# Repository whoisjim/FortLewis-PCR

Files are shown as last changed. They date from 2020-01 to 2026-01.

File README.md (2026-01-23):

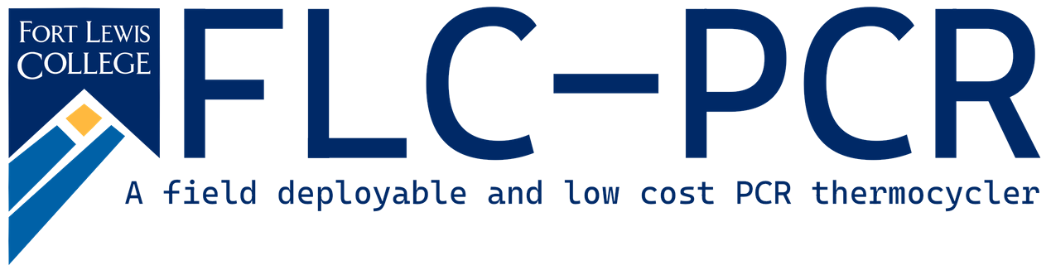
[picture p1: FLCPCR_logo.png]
FLCPCR logo


FLC-PCR is a field deployable and low cost PCR thermocycler developed by students at Fort Lewis College. Polymerase chain reaction (PCR) is the process of duplicating a strand of DNA millions of times. After the DNA has been amplified analysis can be performed to detect pathogens and other DNA related characteristics. Performing PCR on a strand of DNA involves placing the sample in a chemical solution. Then repeating the raising and lowering the temperature duplicates the DNA. Raising the temperature splits the strands and lowering the temperature allows the chemicals to reform the other half of each DNA strand.

## Student Members

- James Ferguson
- Jesse Duran
- Wesley Killinen
- Gavin Wakefield
- Farjana Showme

## Faculty Advisors

- Jason Wagner
- Caroline Kulesza
- Christie Chatterley
- Yiyan Li

## Folder Descriptions

- **CAD:** SOLIDWORKS design files for the the lid and heating block.
- **Circuts:** EAGLE PCB design files for the  PCB microcontroller.
- **DataRecordingAndGraphing:** Recorded data and python scripts for graphing and analysis.
- **Papers:** Project documentation that was presented at weekly meetings or conferences etc.
- **Parts:** Datasheets for components.
- **Software:** The programs that run on the FLC-PCR system.

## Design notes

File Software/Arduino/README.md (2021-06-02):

# Arduino software

The three ATmega328p scripts are as follows.

- PCRControl

  Manages the moment to moment temperature. Control of the system is performed through serial UART communication.

- Serial Commands

  - `whoami\n` prints an identification string.
  - `d\n` request a data point form the system of the format `[Block Temperature] [PWM] [Lid Temperature]\n`.
  - `verbose\n` toggles sending a data point of every tic of the format `[Block Temperature] [PWM] [Lid Temperature]\n`.
  - `pid\n` toggles sending a data point of every tic of the format `[Target Temperature] [Block Temperature] [PWM]\n`.
  - `state\n` sends `0\n` of peltier off, `1\n` for peltier on.
  - `offl\n` Turns the lid off.
  - `offp\n` Turns the peltier off.
  - `off\n` Turns the peltier and lid off.
  - `onl\n` Turns the lid on.
  - `onp\n` Turns the peltier on.
  - `on\n` Turns the peltier and lid on.
  - `pt[value]\n` Sets the target block temperature
  - `pia[value]\n` Sets the weighting for the Block Temperature moving average. 1 is minimum.
  - `poa[value]\n` Sets the weighting for the PWM moving average. 1 is the minimum.
  - `plc[value]\n` Sets the low bound for PWM. -255 is the minimum.
  - `plh[value]\n` Sets the high bound for PWM. 255 is the maximum.

- PCRDummy

  Fakes PCRControl missing some commands. Out of data

- EfficiencyTest

  For measuring System power consumption and thermal output. Does not work with FLC-PCR PCB rev1.

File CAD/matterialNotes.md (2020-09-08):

# materials
[link wiki](https://en.wikipedia.org/wiki/List_of_thermal_conductivities)
[link toolbox](https://www.engineeringtoolbox.com/insulation-temperatures-d_922.html)
## Polyurethane foam 
too low maximum temperature
## Silica aerogel
too hard to make, too expensive, too fragile

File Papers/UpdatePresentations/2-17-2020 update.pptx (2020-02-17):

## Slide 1

Old Block

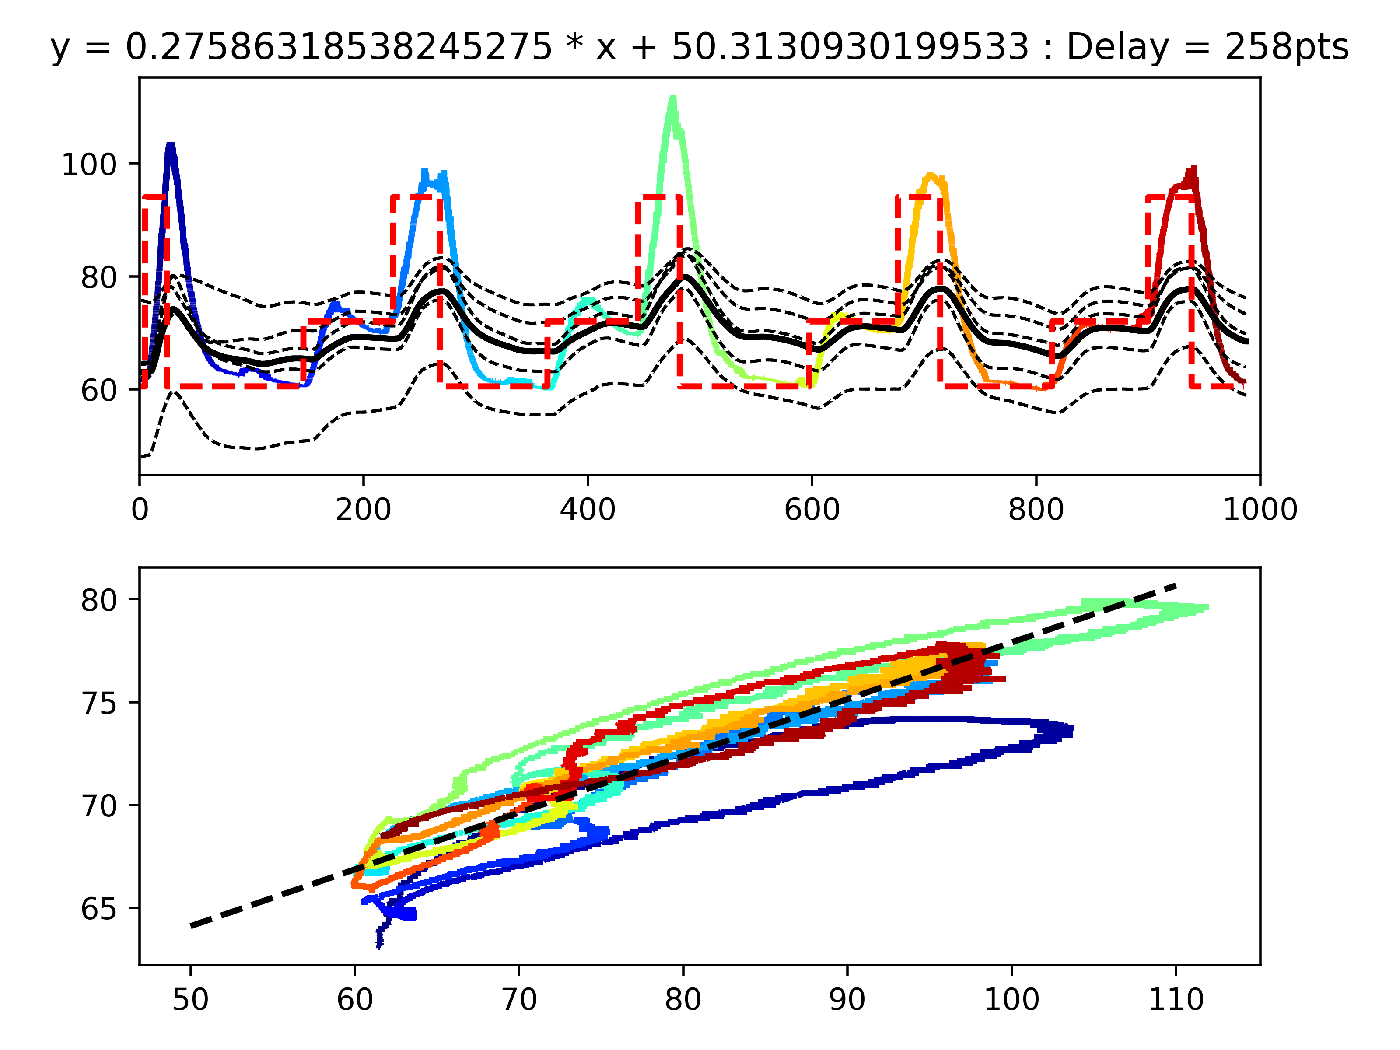
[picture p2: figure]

Bio Rad Block

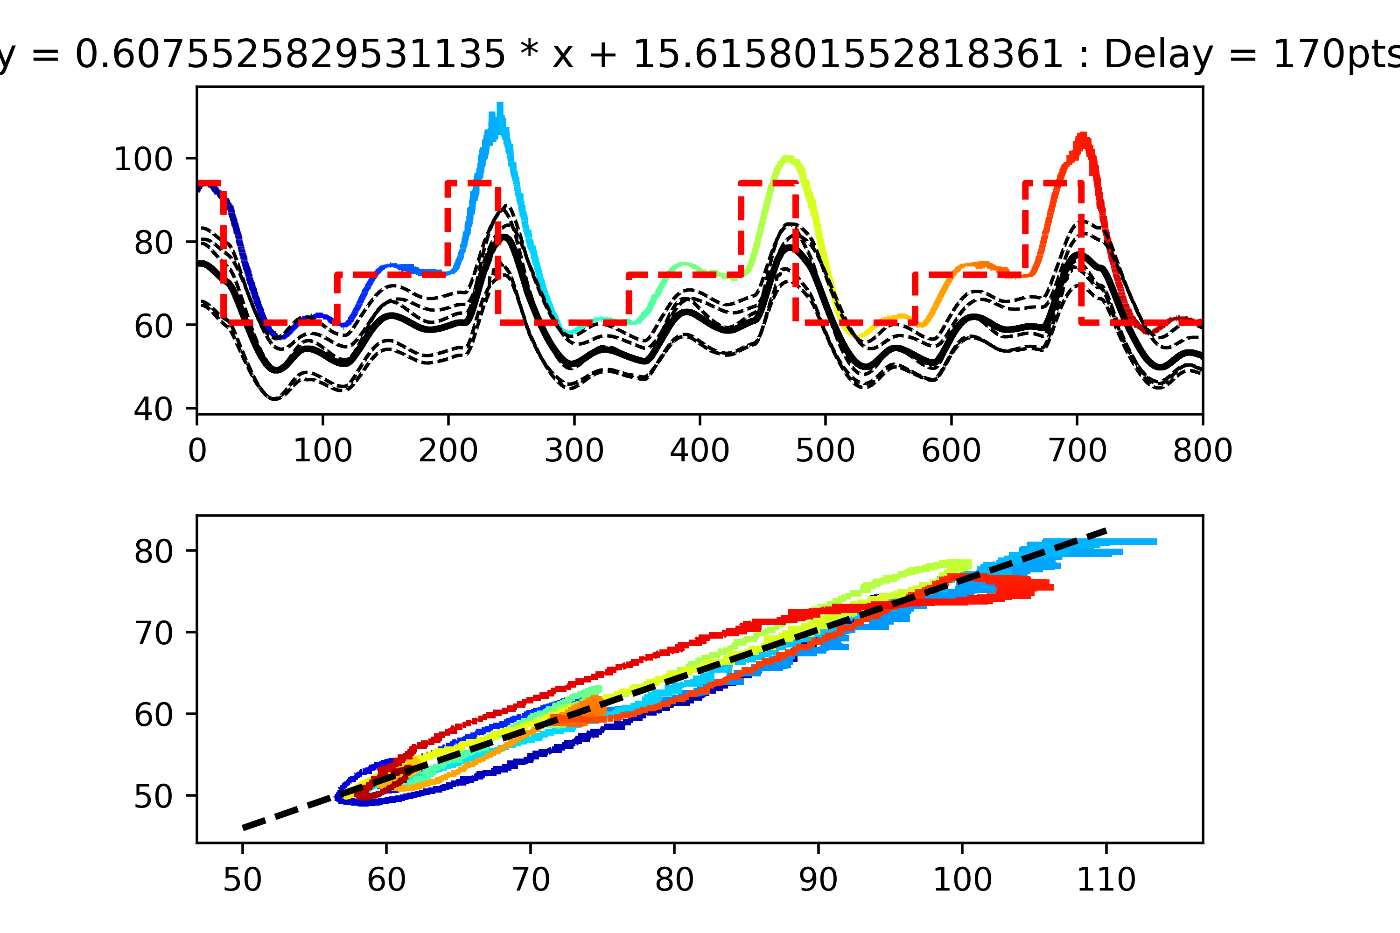
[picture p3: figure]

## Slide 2

After Calibration

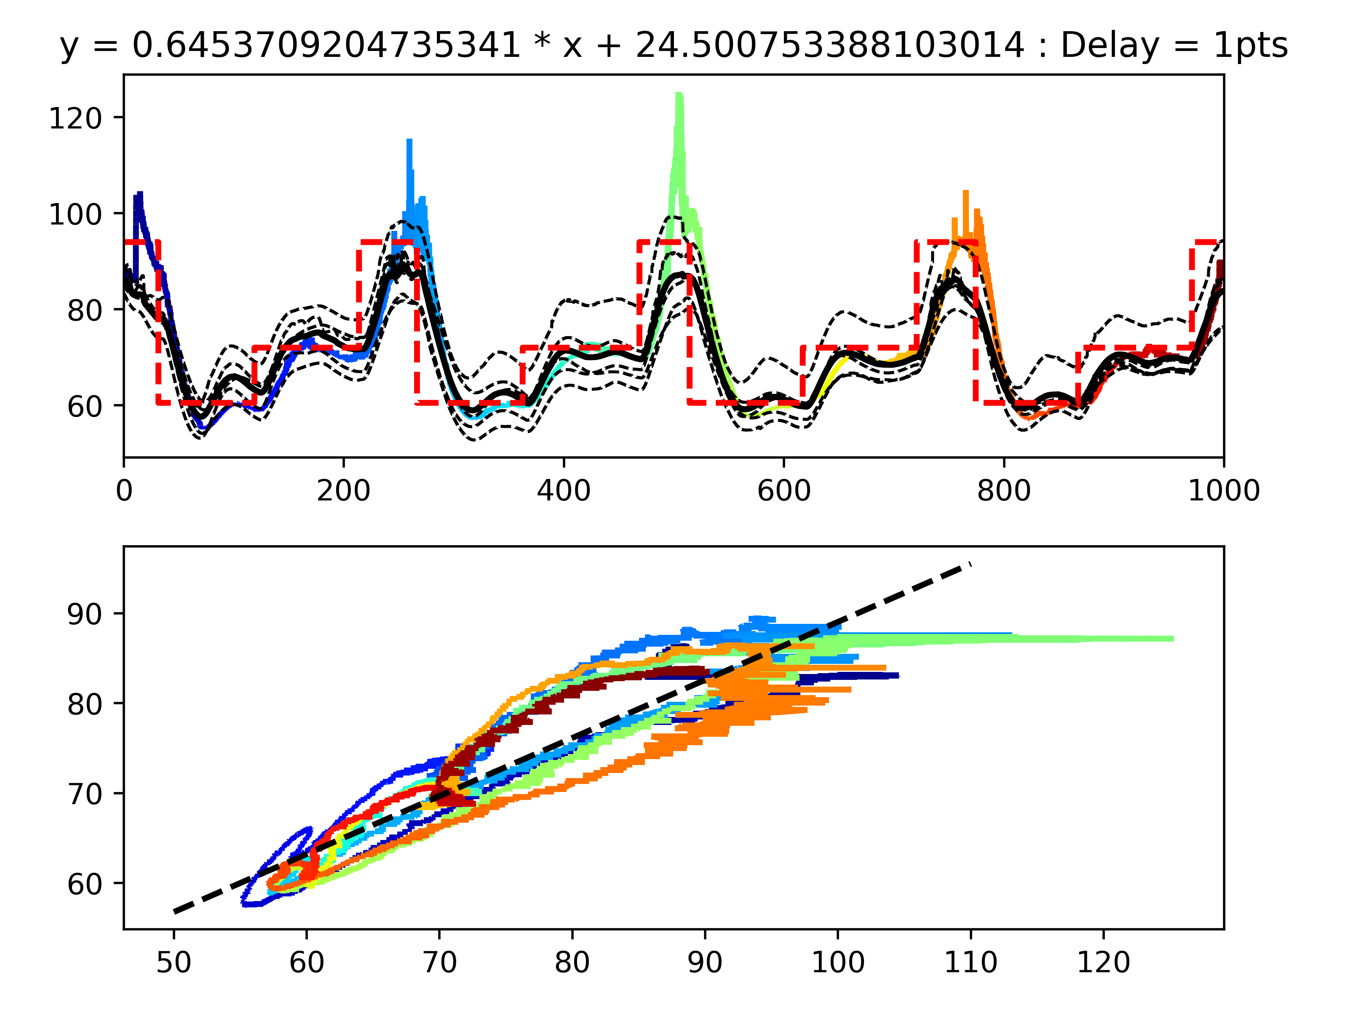
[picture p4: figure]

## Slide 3

Touch Screen Concept

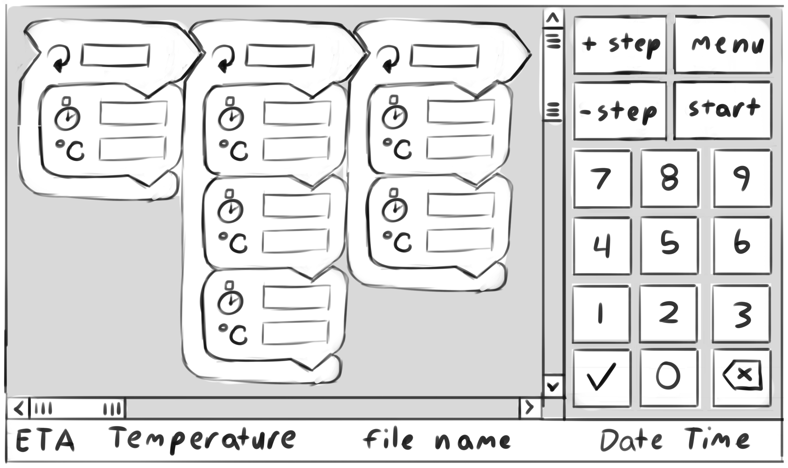
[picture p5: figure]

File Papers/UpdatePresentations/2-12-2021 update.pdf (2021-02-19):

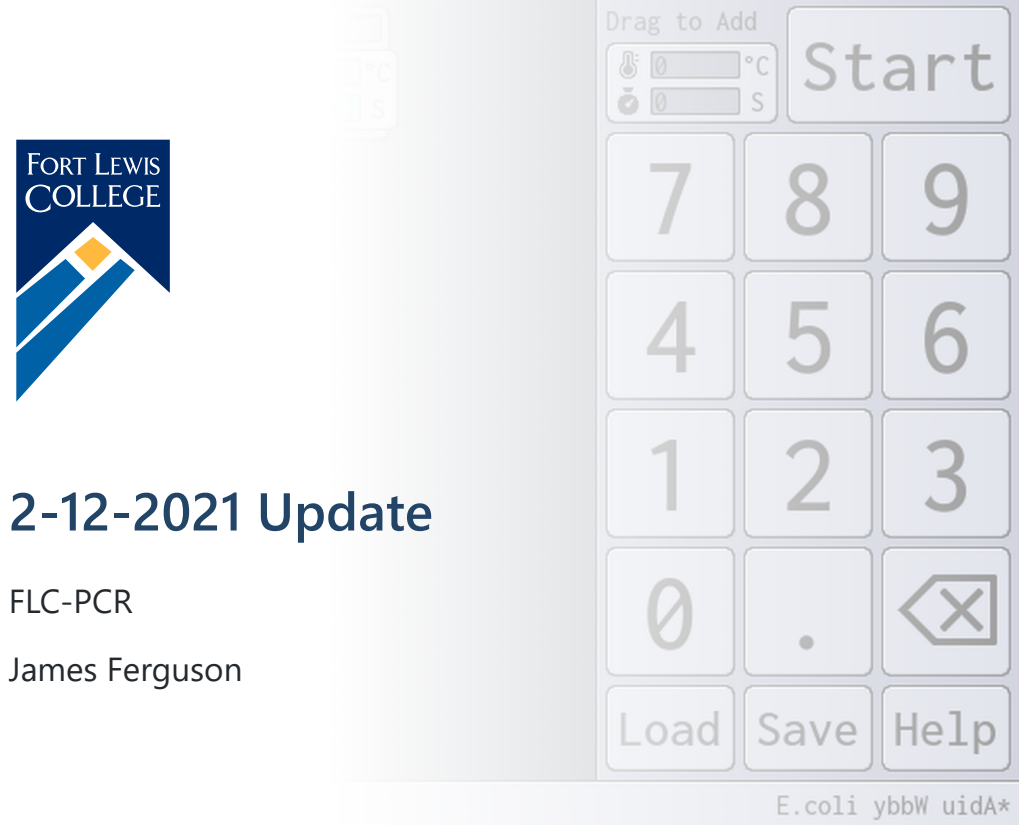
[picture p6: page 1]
2-12-2021 Update; FLC-PCR; James Ferguson

## Last Week

Cleaned lab
Wired thermistors and SSR

## Todo

Finish wiring
Mount Pi and display
Cut holes for vents, switch and power Re-run temperature calibration
Run PCR experiment
Finish fixing UI blocking bug

## End

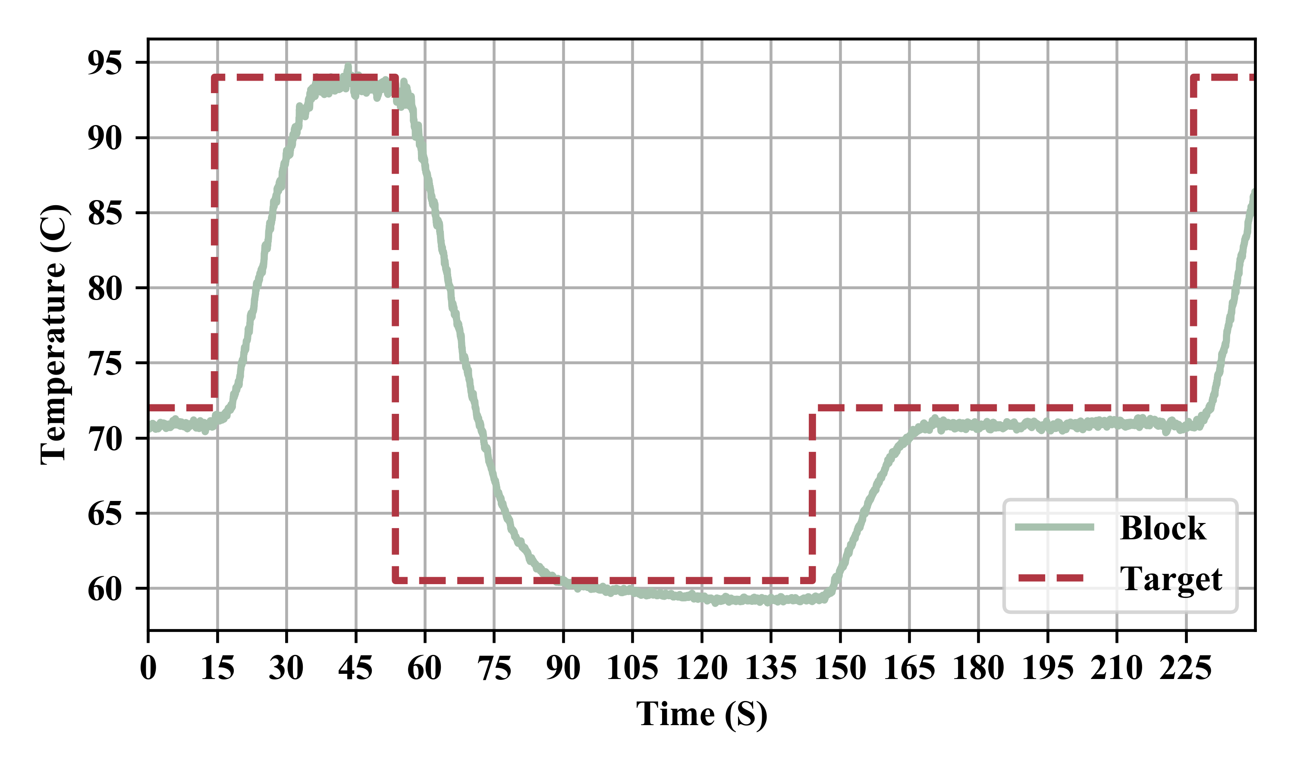
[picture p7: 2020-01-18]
Papers/IEEE_EMBC_2020/CycleTemp.png

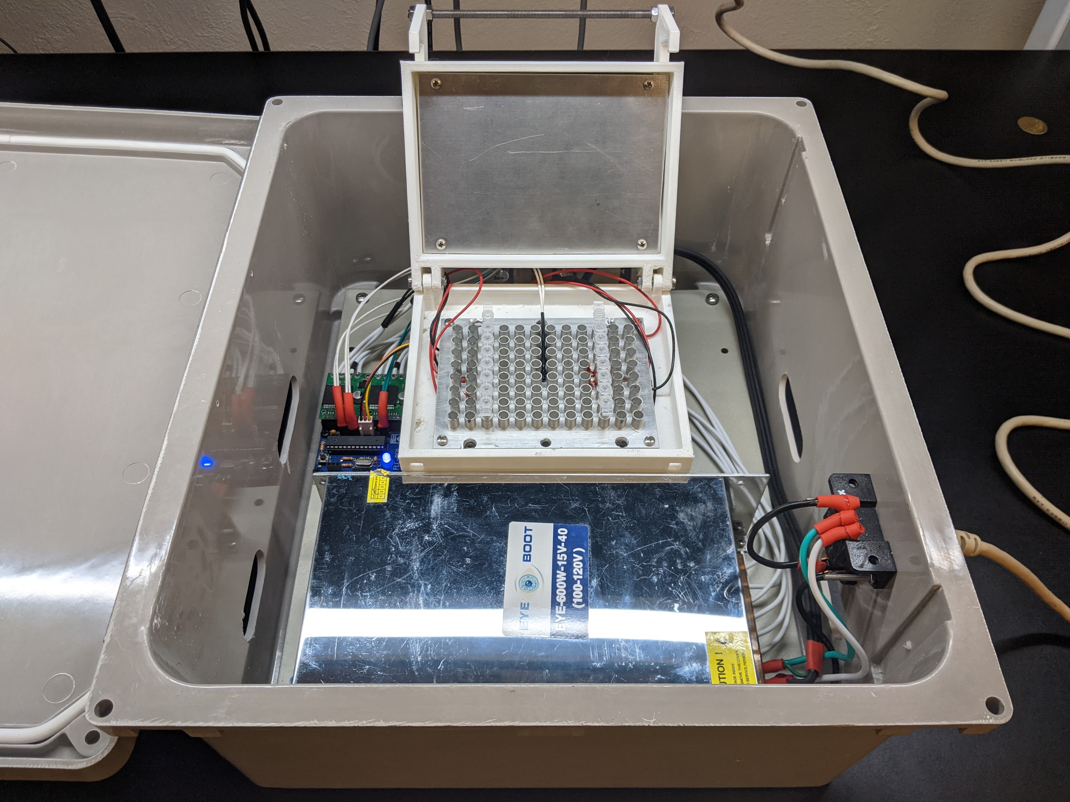
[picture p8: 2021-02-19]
Papers/MiscFigures/OpenLid.jpg

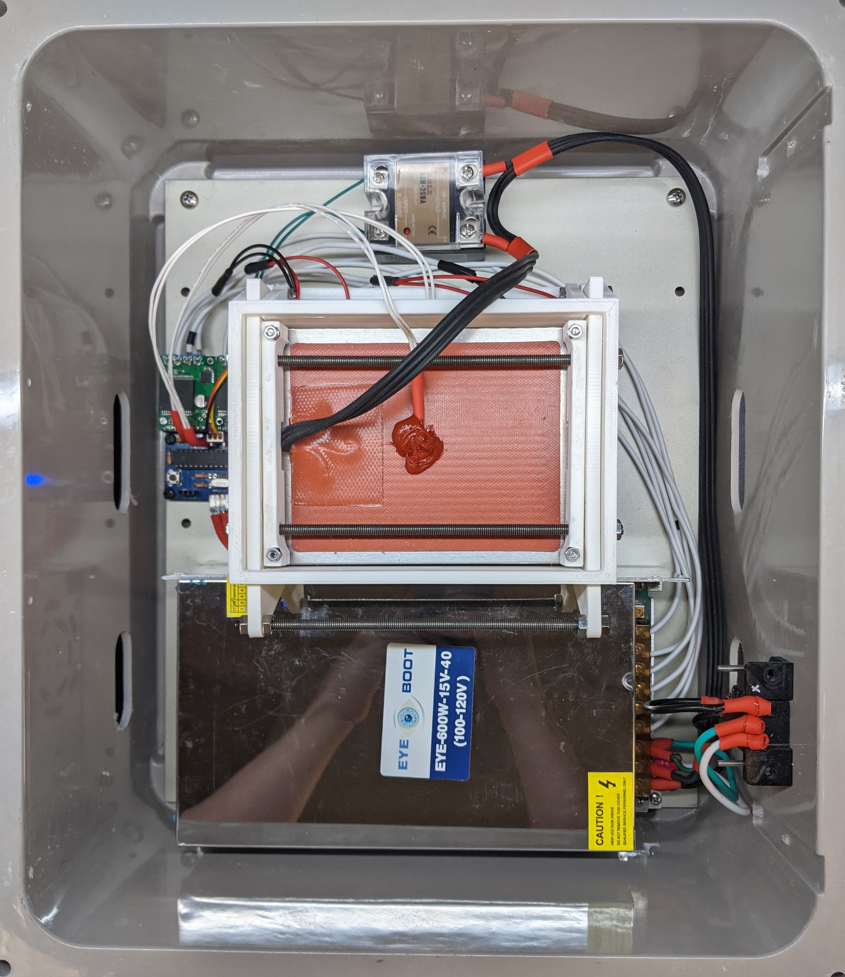
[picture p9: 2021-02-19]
Papers/MiscFigures/TopDonw.jpg

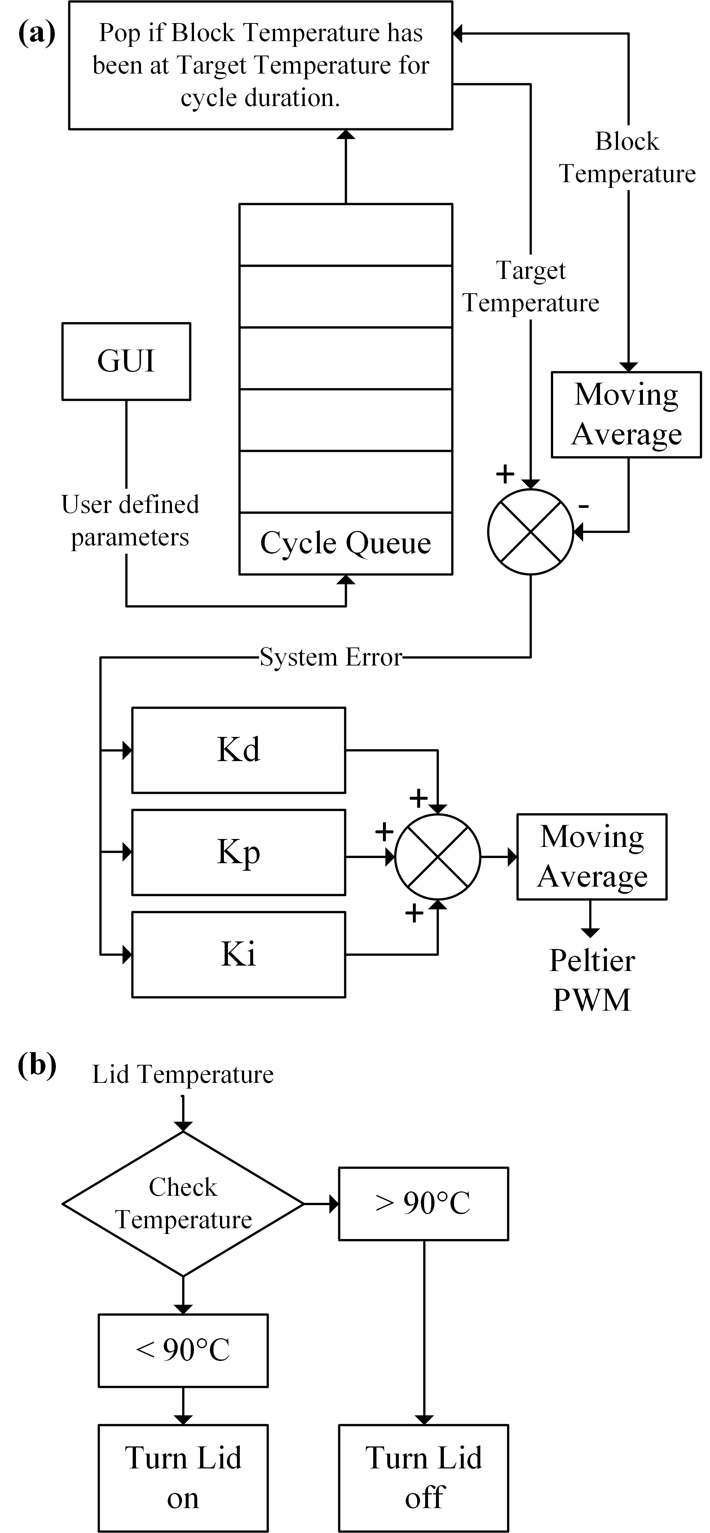
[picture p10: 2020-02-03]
Papers/IEEE_EMBC_2020/SoftwareFigure.png

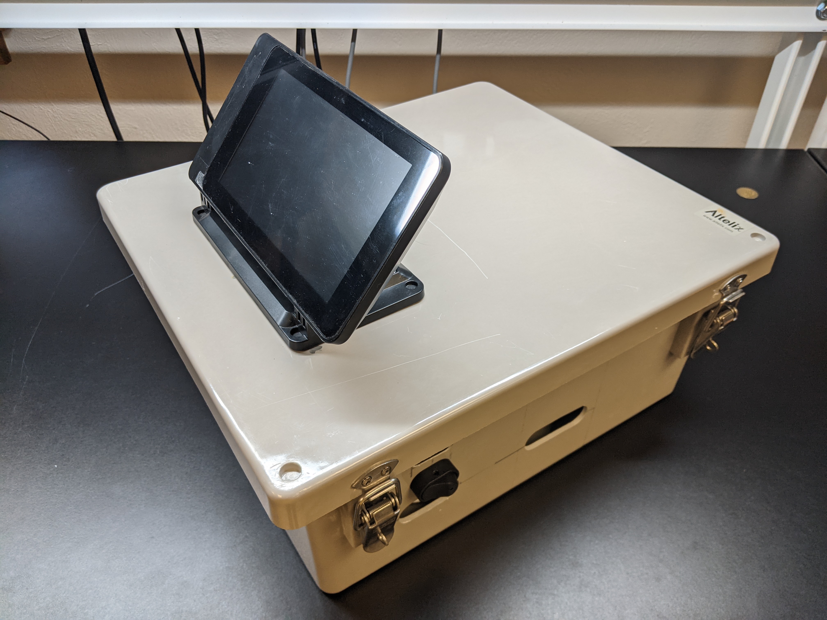
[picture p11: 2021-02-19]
Papers/MiscFigures/ClosedBox.jpg

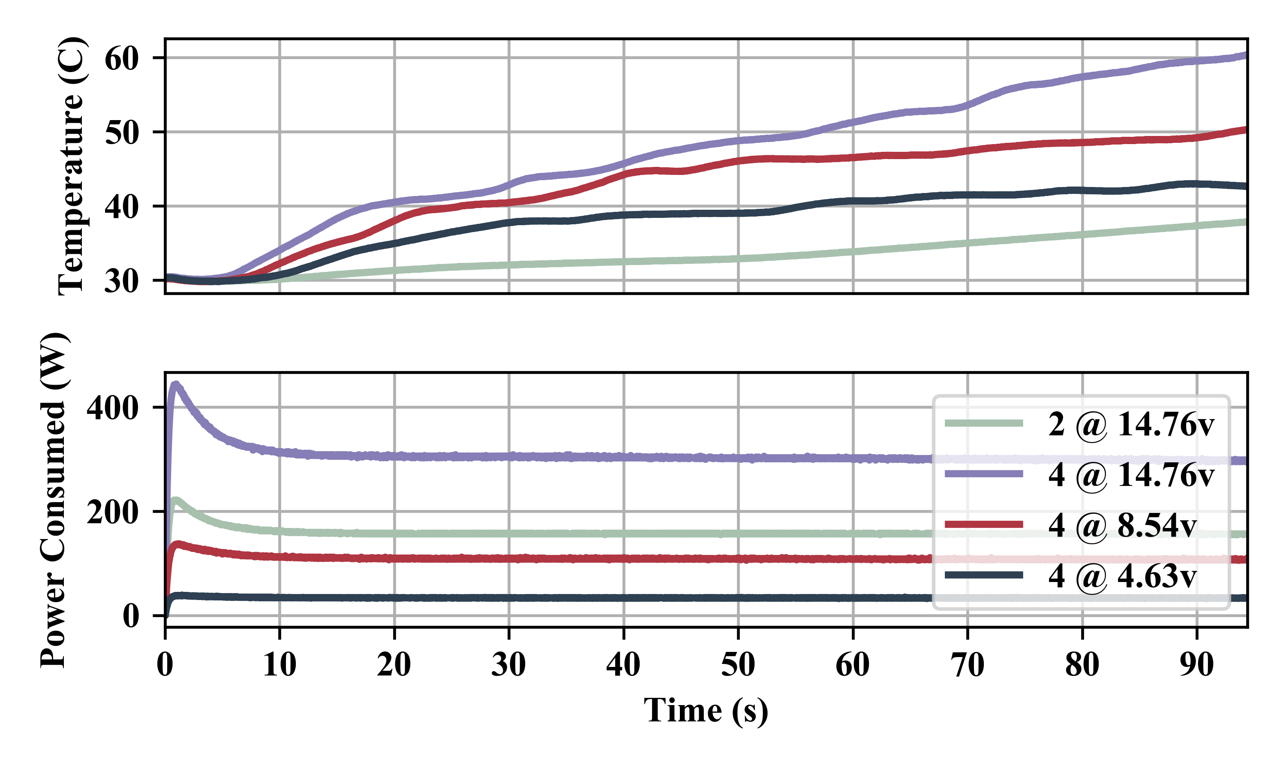
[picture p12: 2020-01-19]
Papers/IEEE_EMBC_2020/efficiency.png

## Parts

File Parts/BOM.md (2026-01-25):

## Bill of Materials (BOM)

| Part Name | Qty | Price | Link |
| :--- | :---: | :---: | :--- |
| **DC to DC Buck Converter** (LM2596)| 2 | $3 | [link](https://www.addicore.com/products/lm2596-step-down-adjustable-dc-dc-switching-buck-converter?srsltid=AfmBOooQSraliBIKv5gF3spnymH-tKSkWzfcQbITQsxnJpUuq1cjG25o) |
| **ASH-25DA Solid State Relay** | 1 | $4 | [Link](https://www.finglai.com/products/relays/solid-state-relays/ASH-DA/ASH-25DA.html?srsltid=AfmBOooy620NcFnOeXSHH8m7hawaNWIw9jwdrxW-gYunpyJ3sHUVVo7X) |
| **Pin Heatsink** (Modified) | 1 | $25 | [Link](https://www.digikey.com/en/products/detail/fischer-elektronik/ICK-S-98-x-98-x-45/26281966) |
| **Silicon Heated Pad** (250W 120V) | 1 | $38 | [Link](https://www.oemheaters.com) |
| **Peltier Modules** (12711-9L31-09CQ) | 4 | $40 | [Link](https://customthermoelectric.com/12711-9l31-09cq-thermoelectric-peltier-module.html) |
| **Current Drivers** (VNH5019) | 2 | $40 | [link](https://www.pololu.com/product/1451) |
| **DC Axial Fan** (92 mm) | 1 | $42 | [Link](https://catalog.orientalmotor.com/item/all-categories-legacy-products/mds-md-series-dc-axial-fans-legacy/md925a-12s?srsltid=AfmBOooDjdUvpDPdjT095zmg7Q5sdXkaaW1B-wEfiyC-99xTTWa7jprv) |
| **ABS Enclosure** (Modified)  | 1 | $46 | [Link](https://www.homedepot.com/p/VEVOR-Electrical-Junction-Box-16-93-x-12-99-x-7-09-in-ABS-Plastic-Electrical-Enclosure-Box-Hinged-Cover-Stainless-Steel-Latch-SLJXHABS16X1GLKCVV0/330552930?source=shoppingads&locale=en-US&fp=ggl&srsltid=AfmBOopQ2WKE1sXIfLH7F72C7fyTCmVs2Y0Q0Ud4duK2vAz2ntJcRd9vvoA) |
| **12V 40A 500W Power Supply** | 1 | $50 | [Link](https://www.newegg.com/p/2YK-006B-00036?item=9SIA9PMED37358) |

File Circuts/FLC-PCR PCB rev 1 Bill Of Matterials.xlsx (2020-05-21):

FLC-PCR Main Board rev 1 Bill Of Matterials
Item | amount | allreaddy have | Unit Price | Price | link | notes
100nF Capacitor | 2 | no | $0.35 | $0.70 | https://www.sparkfun.com/products/96 | I know there are a few of these laying around the school but I don’t have any here with me.
16MHz Resonator | 1 | no | $0.95 | $0.95 | https://www.sparkfun.com/products/9420
DIP Sockets Solder Tail - 28-Pin | 1 | no | $0.95 | $0.95 | https://www.sparkfun.com/products/7942 | I know there are a few of these laying around the school but I don’t have any here with me.
Break Away Male Headers - Right Angle | 1 | no | $1.95 | $1.95 | https://www.sparkfun.com/products/553
Header - 10-pin Female | 2 | no | $0.50 | $1.00 | https://www.sparkfun.com/products/11896
Break Away Male Headers - Straight | 1 | no | $1.50 | $1.50 | https://www.sparkfun.com/products/116 | I know there are a few of these laying around the school but I don’t have any here with me.
0.6mm Button | 1 | yes | $0.00 | $0.00
10kΩ Resistor | 3 | yes | $0.00 | $0.00
1kΩ Resistor | 1 | yes | $0.00 | $0.00
1MΩ Resistor | 1 | yes | $0.00 | $0.00
5mm LED | 1 | yes | $0.00 | $0.00
ATmega328P | 1 | yes | $0.00 | $0.00
 |  |  | Total Price: | $7.05

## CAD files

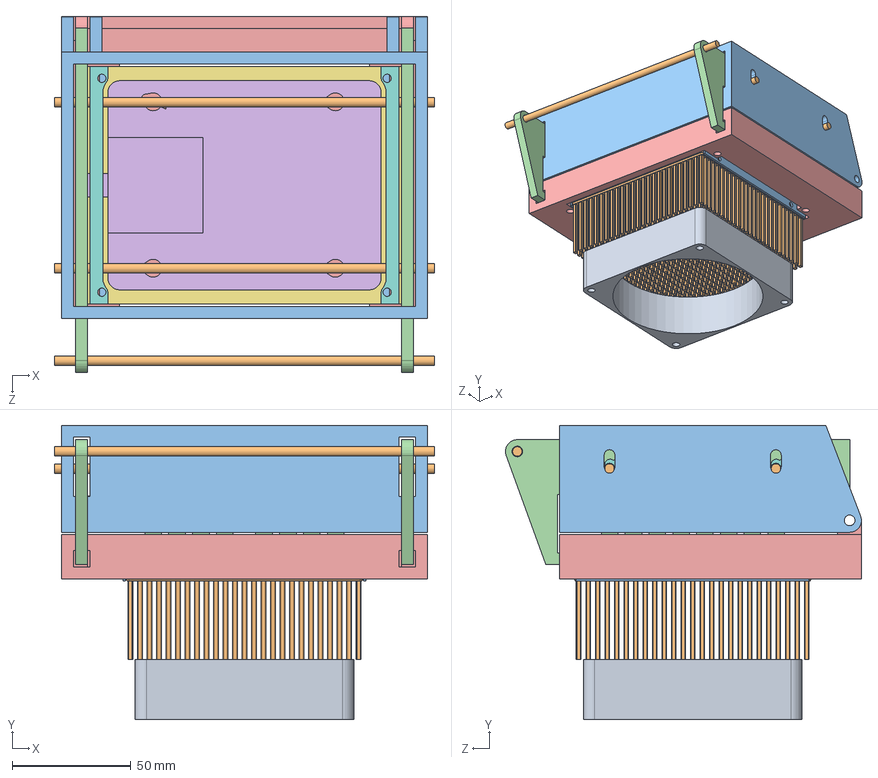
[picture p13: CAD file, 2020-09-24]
CAD/FLC-PCR-NEMA.SLDASM
160.0 x 123.8 x 149.8 mm
md924a-12s-f1
fs10040a
fs10040a-bracket x 2
HollowBlock_v5
PCR Tube x 4
Model-16-Engine-Preheater
Lid-Plate
Lid-Internal-Side x 2
Lid-Spring x 4
m4-Lid-Rod x 3
Lid-Body
Lid-Latch x 2
Body-Frame
12711-9L31-10CQ x 4

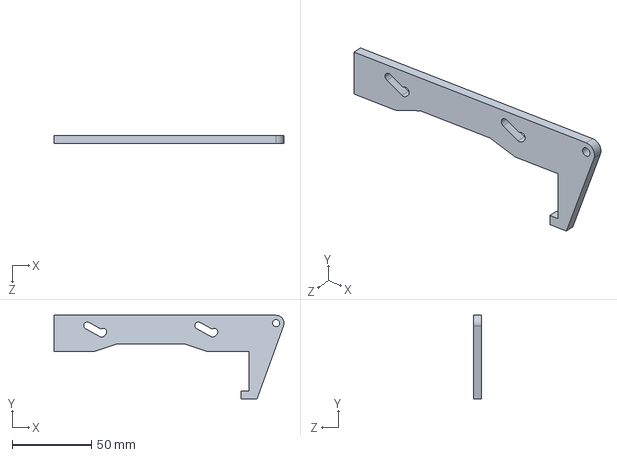
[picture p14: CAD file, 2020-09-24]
CAD/Lid-Latch.SLDPRT
145.0 x 52.6 x 5.00 mm

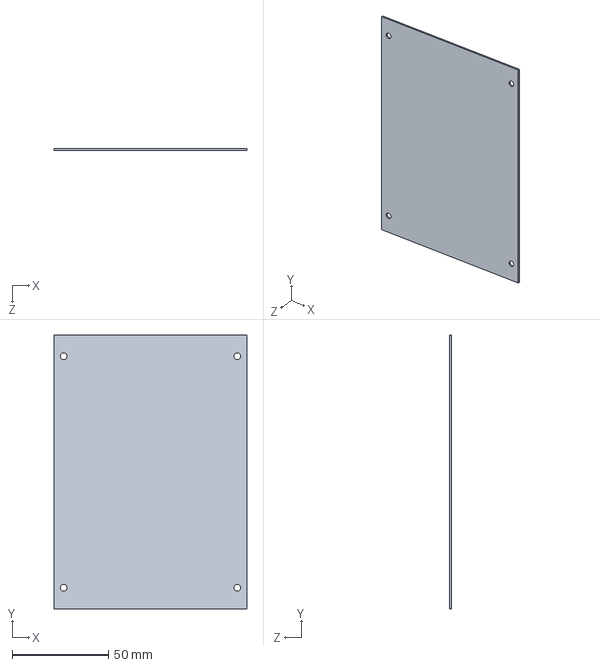
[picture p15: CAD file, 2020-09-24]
CAD/Lid-Plate.sldprt
100.0 x 142.0 x 1.00 mm

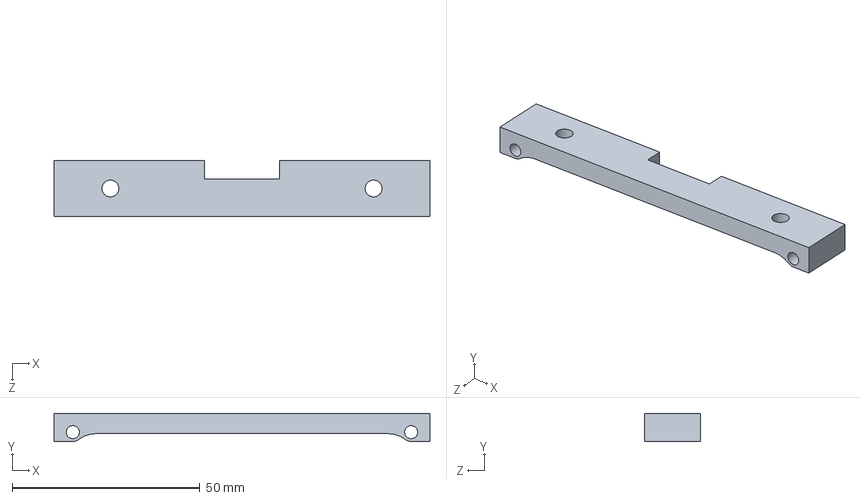
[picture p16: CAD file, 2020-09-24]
CAD/Lid-Internal-Side.sldprt
100.0 x 7.50 x 15.0 mm

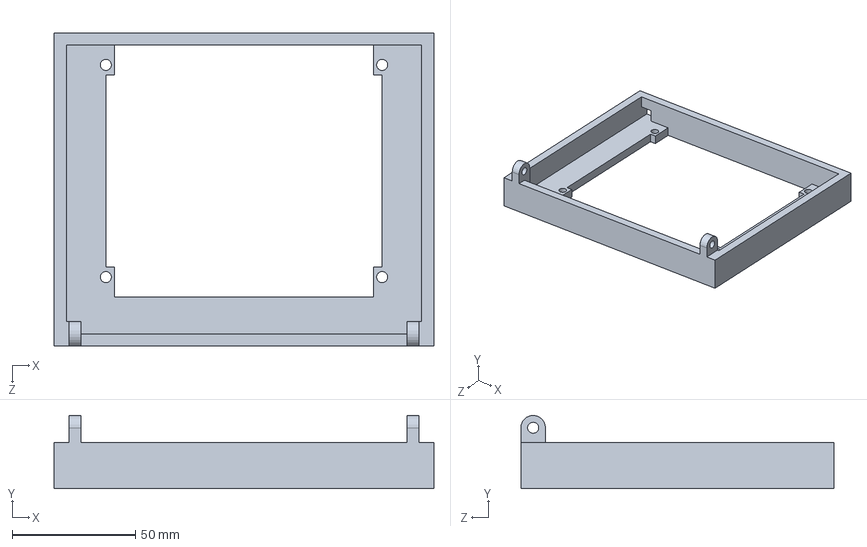
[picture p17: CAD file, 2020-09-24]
CAD/Body-Frame.SLDPRT
154.0 x 29.7 x 127.0 mm

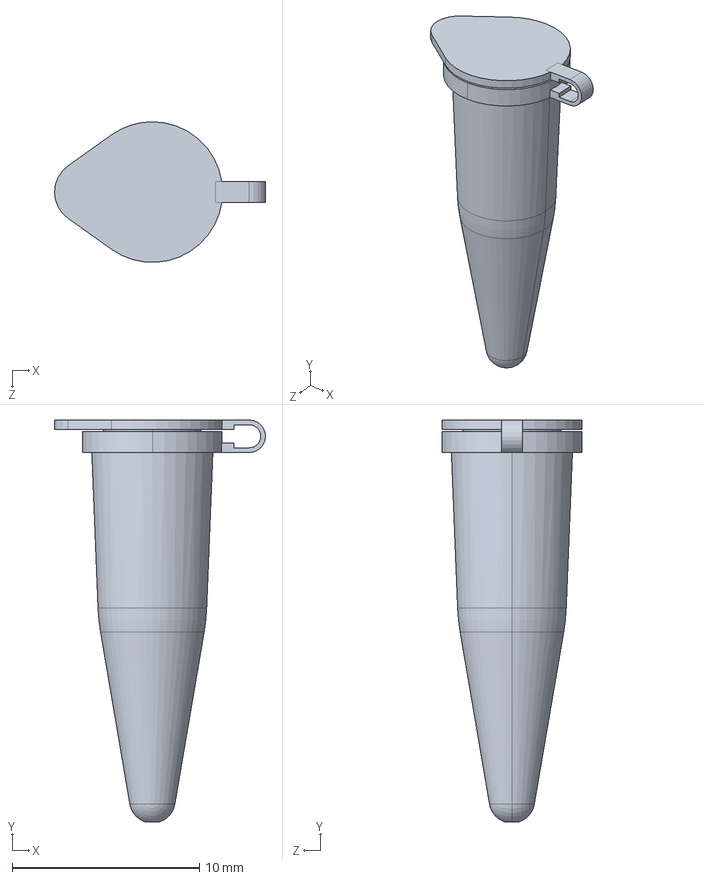
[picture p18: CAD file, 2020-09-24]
CAD/PCR Tube.SLDPRT
11.3 x 21.5 x 7.51 mm

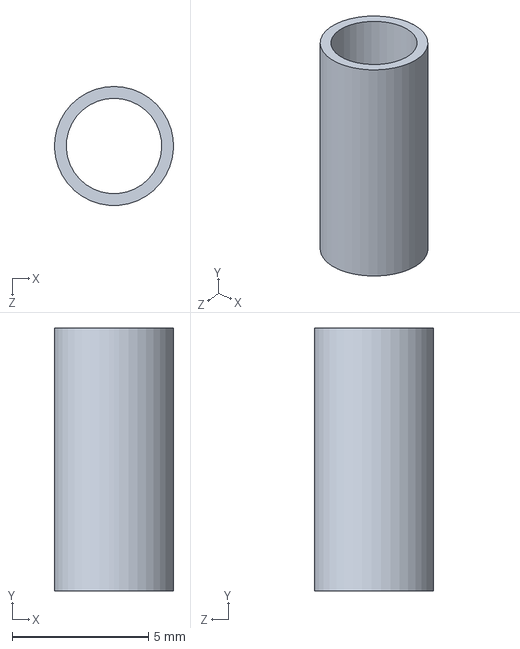
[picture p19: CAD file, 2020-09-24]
CAD/Lid-Spring.SLDPRT
4.37 x 9.65 x 4.37 mm

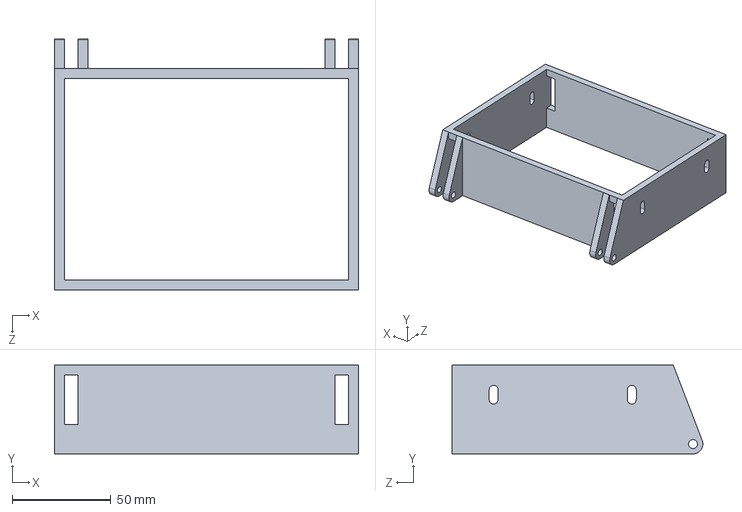
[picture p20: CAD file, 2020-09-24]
CAD/Lid-Body.SLDPRT
154.0 x 45.0 x 127.0 mm

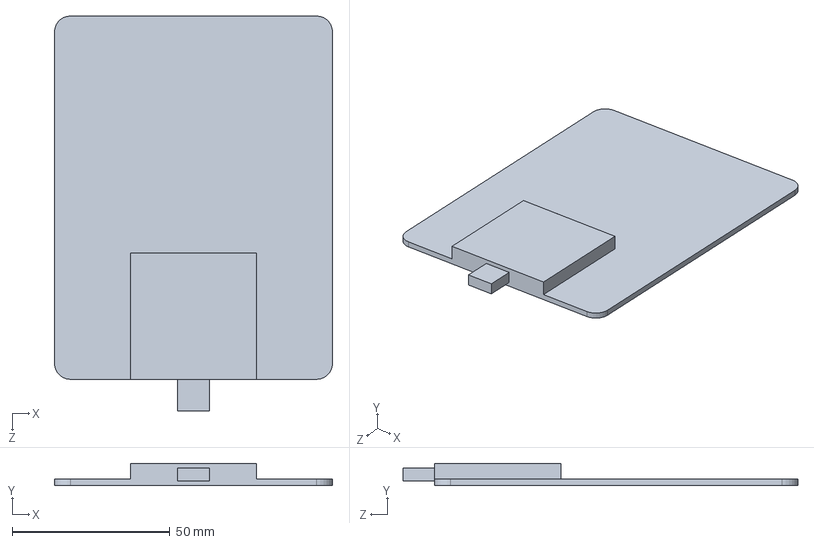
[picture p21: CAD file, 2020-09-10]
CAD/Model-16-Engine-Preheater.SLDPRT
88.0 x 7.00 x 125.0 mm

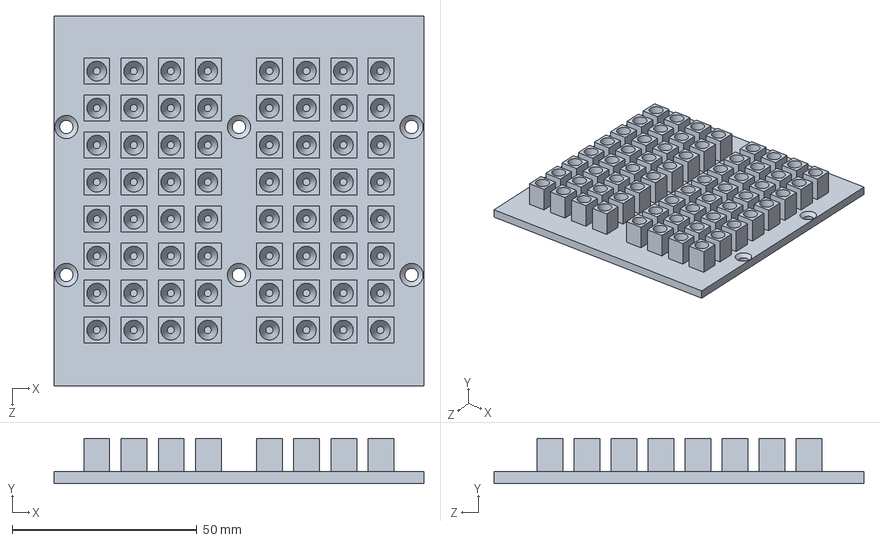
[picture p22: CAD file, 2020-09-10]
CAD/HollowBlock_v5.SLDPRT
100.0 x 12.2 x 100.0 mm

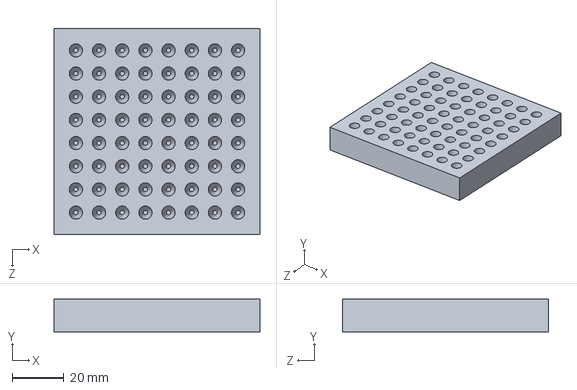
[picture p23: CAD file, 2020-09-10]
CAD/HeatBlock_solid.SLDPRT
80.0 x 12.7 x 80.0 mm

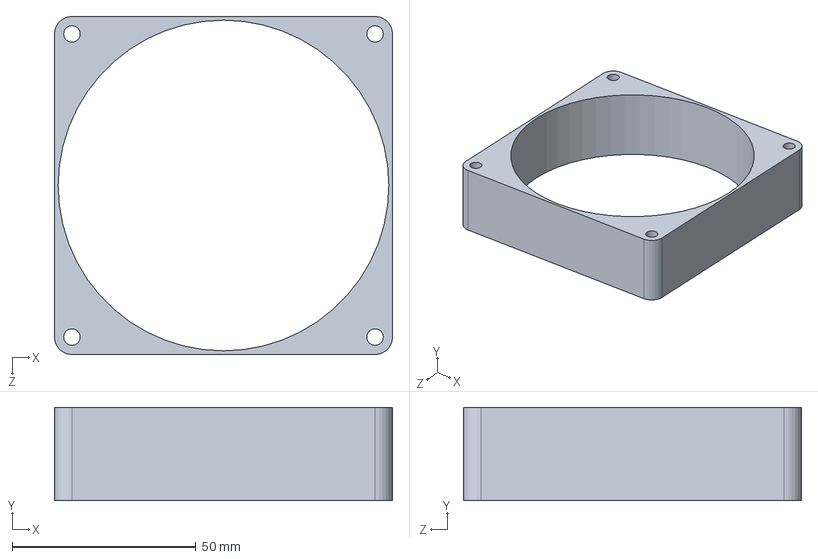
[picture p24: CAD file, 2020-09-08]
CAD/md924a-12s-f1.SLDPRT
92.0 x 25.4 x 92.0 mm

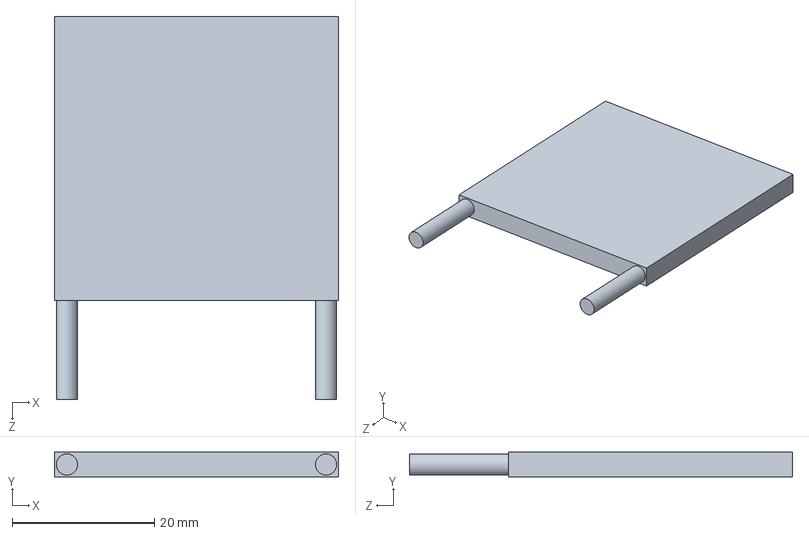
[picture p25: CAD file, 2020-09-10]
CAD/12711-9L31-10CQ.SLDPRT
40.0 x 3.50 x 54.0 mm

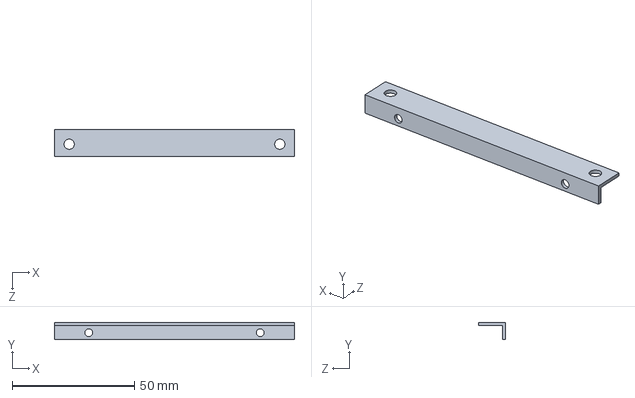
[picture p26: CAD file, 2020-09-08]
CAD/fs10040a-bracket.SLDPRT
98.0 x 7.00 x 11.0 mm

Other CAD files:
CAD/m4-Lid-Rod.sldprt
CAD/HeatBlock draft1.SLDDRW

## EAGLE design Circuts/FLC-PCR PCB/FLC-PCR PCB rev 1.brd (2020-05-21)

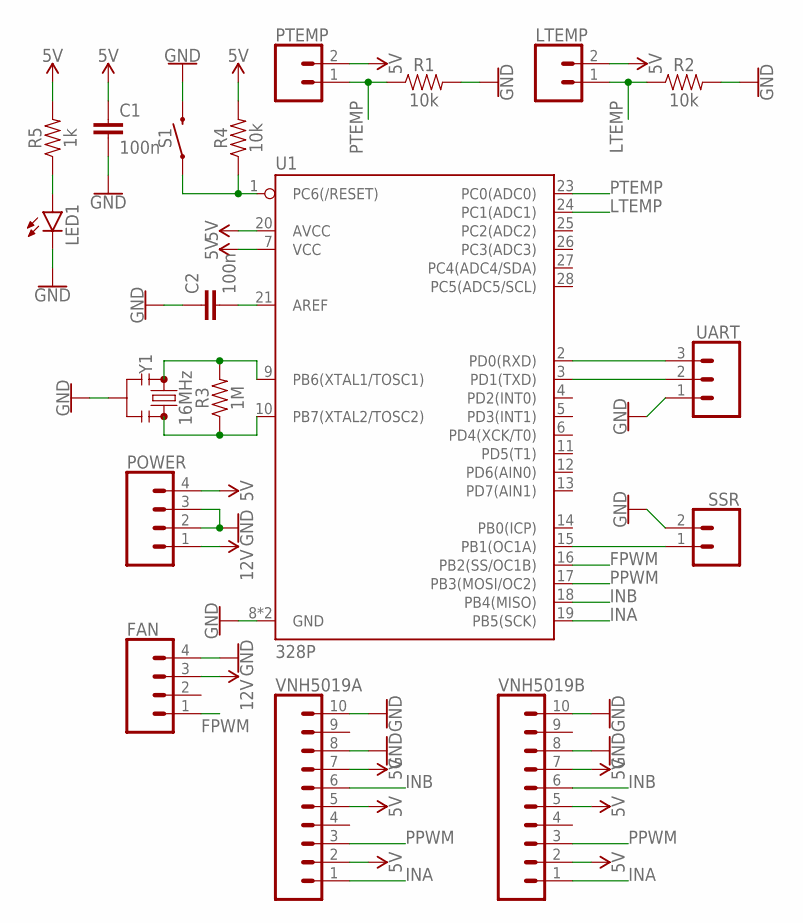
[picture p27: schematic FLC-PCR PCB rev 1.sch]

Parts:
C1, C2: 100n; C025-050X050
FAN: CONN_04PTH; 1X04
LED1: LED5MM
LTEMP: CONN_02; 1X02
POWER: CONN_04PTH; 1X04
PTEMP: CONN_02; 1X02
R1, R2, R4: 10k; AXIAL-0.3
R3: 1M; AXIAL-0.3
R5: 1k; AXIAL-0.3
S1: MOMENTARY-SWITCH-SPST-PTH-6.0MM; TACTILE_SWITCH_PTH_6.0MM
SSR: CONN_02; 1X02
U1: 328P; DIP28
UART: CONN_03; 1X03
VNH5019A, VNH5019B: CONN_10"; 1X10
Y1: 16MHz; RESONATOR-PTH-7.6X3.8

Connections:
5V: C1.1, LTEMP.2, POWER.4, PTEMP.2, R4.P$2 (2), R5.P$2 (2), U1.7 (VCC), U1.20 (AVCC), VNH5019A.2, VNH5019A.5, VNH5019A.7, VNH5019B.2, VNH5019B.5, VNH5019B.7
12V: FAN.3, POWER.1
FPWM: FAN.1, U1.16 (PB2(SS/OC1B))
GND: C1.2, C2.1, FAN.4, LED1.K (C), POWER.2, POWER.3, R1.P$2 (2), R2.P$2 (2), S1.3 (2), SSR.2, U1.8 (GND), U1.22 (GND), UART.1, VNH5019A.8, VNH5019A.10, VNH5019B.8, VNH5019B.10, Y1.2
INA: U1.19 (PB5(SCK)), VNH5019A.1, VNH5019B.1
INB: U1.18 (PB4(MISO)), VNH5019A.6, VNH5019B.6
LTEMP: LTEMP.1, R2.P$1 (1), U1.24 (PC1(ADC1))
unnamed: U1.2 (PD0(RXD)), UART.3
unnamed: U1.3 (PD1(TXD)), UART.2
unnamed: R3.P$2 (2), U1.9 (PB6(XTAL1/TOSC1)), Y1.1
unnamed: R3.P$1 (1), U1.10 (PB7(XTAL2/TOSC2)), Y1.3
unnamed: R4.P$1 (1), S1.1, U1.1 (PC6(/RESET))
unnamed: LED1.A, R5.P$1 (1)
unnamed: C2.2, U1.21 (AREF)
unnamed: SSR.1, U1.15 (PB1(OC1A))
PPWM: U1.17 (PB3(MOSI/OC2)), VNH5019A.3, VNH5019B.3
PTEMP: PTEMP.1, R1.P$1 (1), U1.23 (PC0(ADC0))

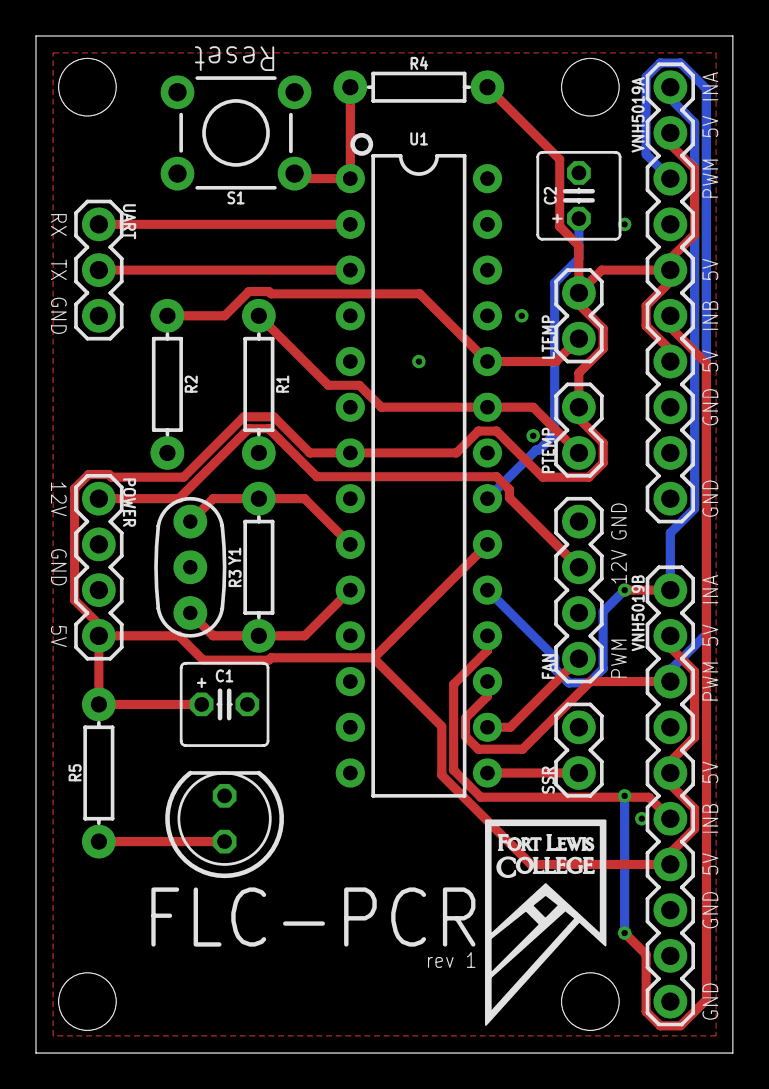
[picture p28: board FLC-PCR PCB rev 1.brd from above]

Board: 2 copper layers, 38.7 x 56.5 mm, 19 parts (0 on the bottom side), 17 nets.

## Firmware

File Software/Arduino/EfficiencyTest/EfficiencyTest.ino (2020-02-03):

#include <math.h>
const int inA = 13; // pin connected to INA on VHN5019
const int inB = 12; // pin connected to INB on VHN5019
const int ppwm = 11; // pin connected to PWM on VHN5019
const int fpwm = 10; // pin connected to PWM on fan
const int thermP = A0; // pin connected to thermal resistor neetwork. see elegooThermalResistorSch.png

bool power = false; // software on/off

double peltierPWM = 0; // the PWM signal * curent direction to be sent to curent drivers for peltier

float avgPTemp = 0; // last average for peltier temperature
int avgPTempSampleSize = 10; // sample size for peltier temperature moving average

double targetPeltierTemp = 30; // the tempature the system will try to move to, in degrees C
double currentPeltierTemp; // the tempature curently read from the thermoristor connected to thermP, in degrees C

// class for creating a pid system
class pid {
  private:
  double kp; // higher moves faster
  double ki; // higher fixes ofset and faster
  double kd; // higher settes faster but creastes ofset
  double kAmbiant; // experimental, fixes ofset?, may remove. leave at zero if unshure
  unsigned long currentTime, lastTime; // the time in millisecconds of this timesep and the last timestep
  double pError, lError, iError, dError; // error values for pid calculations. p: porportional, l: last, i: integerl, d: derivitive
    
  public:
  pid (double proportionalGain = 1, double integralGain = 0, double derivativeGain = 0) {
    kp = proportionalGain; // higher moves faster
    ki = integralGain; // higher fixes ofset and faster
    kd = derivativeGain; // higher settes faster but creastes ofset and amplifies noise
  }
  
  double calculate(double currentTemp, double targetTemp){ // gets tempature and performs pid calculation returns error in degrees C
    lastTime = currentTime;
    currentTime = millis();
    lError = pError;
    pError = targetTemp - currentTemp;
    iError = pError * (double)(currentTime - lastTime);
    dError = (pError - lError) / (double)(currentTime - lastTime);
    return kp * pError + ki * iError + kd * dError;
  }
  void setKp(float value) {
    kp = value;
  }
  void setKi(float value) {
    ki = value;
  }
  void setKd(float value) {
    kd = value;
  }
};

// for creating a tempature sensor
// includes noise reduction
// call resetTemp() before a series of getTemp() calls
// see elegooThermalResistorSch.png for wireing
class TempSensor {
  private:
  int pin;
  double temp;
  double lastK;
  
  public:
  TempSensor(int iPin) { 
    pin = iPin; // the pin that conected to the tempature network
  }
  
  void resetTemp() { // resets saved privois tempature, nessasary if it has been a while since last getTemp()
    int tempReading = analogRead(pin);
    double tempK = log(10000.0 * ((1024.0 / tempReading - 1)));
    lastK = 1 / (0.001129148 + (0.000234125 + (0.0000000876741 * tempK * tempK )) * tempK );
  }

  double getTemp() { // returns the tempature from thermoristor connected to thermP in degrees C, includes noise reduction
    static double spike0u;
    int tempReading = analogRead(pin);
    double tempK = log(10000.0 * ((1024.0 / tempReading - 1)));
    tempK = 1 / (0.001129148 + (0.000234125 + (0.0000000876741 * tempK * tempK )) * tempK ); // kelvin

    //Serial.print(tempK - 273.15);
    //Serial.print(" ");
    
    // noise peak removal
    
    if (tempK - lastK > 0.5 + abs(lastK -299.15) * 0.1) {
      if (spike0u == 0) {
        spike0u = tempK - lastK;
      }
      tempK -= spike0u;
    } else {
      spike0u = 0;
    }

    if (tempK - lastK < -10) {
      tempK += spike0u;
      spike0u = 0;
    }
    
    lastK = tempK;
    
    return (tempK - 273.15); // convert kelvin to celcius
  }
};

// setup pieltier tempature sensor
TempSensor peltierT(thermP);

// setup pieltier PID
pid peltierPID(5, 0.8, 6000);

bool finished = false;
bool start = false;

void setup() {
  // setup serial
  Serial.begin(9600);
  while (!Serial) {
    ; // wait for serial port to connect. Needed for native USB port only
  }

  // setup pins
  pinMode(inA, OUTPUT);
  pinMode(inB, OUTPUT);
  pinMode(ppwm, OUTPUT);
  pinMode(fpwm, OUTPUT);
  pinMode(thermP, INPUT);

  // set initial pin state to off
  digitalWrite(inA, LOW);
  digitalWrite(inB, LOW);
  analogWrite(ppwm, 0);
  analogWrite(fpwm, 0);

  peltierT.resetTemp();
}

void loop() {
  currentPeltierTemp = peltierT.getTemp(); // read pieltier temp
  avgPTemp = ((avgPTempSampleSize - 1) * avgPTemp + currentPeltierTemp) / avgPTempSampleSize; // average input with the last 9 inputs
  peltierPWM = peltierPID.calculate(avgPTemp, targetPeltierTemp); // calculate pid and set to output
  peltierPWM = min(255, max(-255, peltierPWM)); // clamp output between -255 and 255

  if (digitalRead(7) == HIGH) {
    start = true;
  }

  if (start) {
    peltierPWM = 63;
  } else {
    peltierT.resetTemp();
  }

  float pI = analogRead(A1) * 0.065168; // for two driver boards
  float pV = peltierPWM * (15 / 255.0);
  
  // for graphing system state
  Serial.print(avgPTemp);
  Serial.print(" ");
  Serial.print(pV);
  Serial.print(" ");
  Serial.print(pI);
  Serial.print("\n");

  if (currentPeltierTemp > 65) {
    finished = true;
  }

  if (finished) {
    digitalWrite(inA, LOW);
    digitalWrite(inB, LOW);
    analogWrite(fpwm, 1024);
    analogWrite(ppwm, 0);
    return;
  }
  
  if (currentPeltierTemp > 150) {// shut off system if over 150 degrees for safety
    digitalWrite(inA, LOW);
    digitalWrite(inB, LOW);
    analogWrite(fpwm, 1024);
    analogWrite(ppwm, 0);
    return;
  }

  // convert pieltierDelta to pwm, inA, inB, and fan signals
  analogWrite(ppwm, abs(peltierPWM));
  if (peltierPWM > 0) {
    digitalWrite(inA, HIGH);
    digitalWrite(inB, LOW);
    analogWrite(fpwm, 0);
  } else {
    digitalWrite(inA, LOW);
    digitalWrite(inB, LOW);
    analogWrite(fpwm, 255);
  }
}

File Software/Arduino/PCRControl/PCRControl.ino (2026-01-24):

#include "TemperatureSensor.hpp"
#include "PID.hpp"
#include <math.h>

#define SOFTWARE_VERSION "2025.7.7"

// Pin definitions
const int inA = 13;       // Current driver direction pin A
const int inB = 12;       // Current driver direction pin B
const int ppwm = 11;      // Peltier PWM output 
const int fpwm = 10;      // Fan PWM output
const int thermP = A0;    // Thermistor input for Peltier block
const int LidP = A1;      // Thermistor input for heated lid
const int ssr = 9;        // Solid State Relay for lid heater

// System state flags
bool pPower = false;      
bool lPower = false;     
bool verboseState = false;
bool verbosePID = false;  

// PWM and temperature control
double peltierPWM = 0;    
int limitPWMH = 255;   
int limitPWMC = 255;     
int currentFanPWM = 255;  

// Temperature filtering
float avgPTemp = 0;       
float avgPPWM = 0;      
double targetPeltierTemp = 29; 
double currentPeltierTemp;     
double currentLidTemp;        
float alpha = 0.7;        

// Sensors and PID
TemperatureSensor peltierT(thermP);
TemperatureSensor LidT(LidP);
PID peltierPID(0, 0, 0); 

void setup() {
  Serial.begin(115200);
  while (!Serial) { ; }  

  // Initialize digital and PWM pins
  pinMode(inA, OUTPUT);
  pinMode(inB, OUTPUT);
  pinMode(ppwm, OUTPUT);
  pinMode(fpwm, OUTPUT);
  pinMode(thermP, INPUT);
  pinMode(LidP, INPUT);
  pinMode(ssr, OUTPUT);

  // Set initial safe state 
  digitalWrite(inA, LOW);
  digitalWrite(inB, LOW);
  analogWrite(ppwm, 0);
  analogWrite(fpwm, 0);
  digitalWrite(ssr, LOW);

  // Setup PID constraints
  peltierPID.setOutputLimits(-200, 200); // Protects Pelteirs from excess use
  peltierPID.setIntegratorLimit(50);     
}

void handleSerialInput() {
  if (Serial.available() > 0) {
    String incomingCommand = Serial.readString();

    // Identify device/version
    if (incomingCommand == "whoami\n") {
      Serial.print("FLC-PCR software version: ");
      Serial.print(SOFTWARE_VERSION);
      Serial.print("\n");
    }
    // Toggle telemetry modes
    else if (incomingCommand == "verbose\n") {
      verboseState = !verboseState;
    }
    else if (incomingCommand == "pid\n") {
      verbosePID = !verbosePID;
    }
    
    else if (incomingCommand == "d\n") {
      Serial.print(avgPTemp);
      Serial.print(" ");
      Serial.print(avgPPWM);
      Serial.print(" ");
      Serial.print(currentLidTemp);
      Serial.print("\n");
    }
    // Report power status
    else if (incomingCommand == "state\n") {
      Serial.print(pPower ? "ON" : "OFF");
      Serial.print("\n");
    }
    // Power control commands
    else if (incomingCommand == "offl\n") {
      lPower = false;
    }
    else if (incomingCommand == "offp\n") {
      pPower = false;
    }
    else if (incomingCommand == "off\n") {
      pPower = false;
      lPower = false;
    }
    else if (incomingCommand == "onl\n") {
      lPower = true;
    }
    else if (incomingCommand == "onp\n") {
      pPower = true;
      peltierPID.reset(); 
    }
    else if (incomingCommand == "on\n") {
      pPower = true;
      lPower = true;
      peltierPID.reset();
    }
    // Commands coming from SBC
    else if (incomingCommand.substring(0, 2) == "kp") {
      peltierPID.setKp(incomingCommand.substring(2).toFloat());
    }
    else if (incomingCommand.substring(0, 2) == "ki") {
      peltierPID.setKi(incomingCommand.substring(2).toFloat());
    }
    else if (incomingCommand.substring(0, 2) == "kd") {
      peltierPID.setKd(incomingCommand.substring(2).toFloat());
    }
    else if (incomingCommand.substring(0, 2) == "pt") {
      targetPeltierTemp = incomingCommand.substring(2).toFloat();
      peltierPID.reset(); 
    }
    else if (incomingCommand.substring(0, 3) == "plc") {
      limitPWMC = incomingCommand.substring(3).toInt();
    }
    else if (incomingCommand.substring(0, 3) == "plh") {
      limitPWMH = incomingCommand.substring(3).toInt();
    }
  }
}

void loop() {
  handleSerialInput();

  currentLidTemp = LidT.getTemp(115);
  currentPeltierTemp = peltierT.getTemp(targetPeltierTemp);

  if (isnan(currentPeltierTemp) || isinf(currentPeltierTemp)) {
    currentPeltierTemp = avgPTemp;
  }

  // Filter out signal noise
  avgPTemp = alpha * currentPeltierTemp + (1 - alpha) * avgPTemp;

  // PID Computation Loop
  static unsigned long lastPIDTime = 0;
  if (millis() - lastPIDTime >= 150) {
    double error = targetPeltierTemp - avgPTemp;

    // Gain Scheduling: Adjust PID constants based on target and error
    if (error < -2.0) {  // Cooling mode
      peltierPID.setKp(8.0);
      peltierPID.setKi(0.001);
      peltierPID.setKd(35.0);
    }
    else if (error < 0) {  // Fine tuning cooling 
      peltierPID.setKp(12.0);
      peltierPID.setKi(0.6);
      peltierPID.setKd(35.0);
    }
    else { 
      if (targetPeltierTemp >= 90) { 
        peltierPID.setKp(38);
        peltierPID.setKi(1.5);
        peltierPID.setKd(20);
        peltierPID.setIntegratorLimit(40);
      }
      else if (targetPeltierTemp >= 70) { 
        peltierPID.setKp(27);
        peltierPID.setKi(0.9);
        peltierPID.setKd(37);
        peltierPID.setIntegratorLimit(50);
      }
      else {
        peltierPID.setKp(21);
        peltierPID.setKi(0.6);
        peltierPID.setKd(41);
        peltierPID.setIntegratorLimit(50);
      }
    }
    peltierPWM = peltierPID.calculate(avgPTemp, targetPeltierTemp);
    avgPPWM = peltierPWM;
    lastPIDTime = millis();
  }

  peltierPWM = constrain(peltierPWM, -limitPWMC, limitPWMH);
  if (isnan(peltierPWM) || isinf(peltierPWM)) {
    peltierPWM = avgPPWM;
  }

  // Hardware control
  if (pPower && currentPeltierTemp <= 150) { 
    
    // Lower fan speed at high heat 
    if (avgPTemp >= 90 || targetPeltierTemp >= 90) {
      currentFanPWM = 100;  
    }
    else {
      currentFanPWM = 255; 
    }

    analogWrite(fpwm, currentFanPWM);
    analogWrite(ppwm, abs((int)peltierPWM)); 

    // Current driver Control
    if (peltierPWM > 0) { 
      digitalWrite(inA, HIGH);
      digitalWrite(inB, LOW);
    } else {              
      digitalWrite(inA, LOW);
      digitalWrite(inB, HIGH);
    }
  }
  else {
    // Safety shutdown
    digitalWrite(inA, LOW);
    digitalWrite(inB, LOW);
    analogWrite(ppwm, 0);
    analogWrite(fpwm, 0);
    if (!pPower) {
      peltierPID.reset();
    }
  }

  // Solid state relay for heated lid
  if (lPower) {
    digitalWrite(ssr, (currentLidTemp < 115) ? HIGH : LOW); // Setting Lid Temperature
  } else {
    digitalWrite(ssr, LOW);
  }

  // UI/Serial update loop
  static unsigned long lastUIUpdateTime = 0;
  if (millis() - lastUIUpdateTime >= 100) {
    if (verboseState) {
      Serial.print(currentPeltierTemp);
      Serial.print(" ");
      Serial.print(peltierPWM);
      Serial.print(" ");
      Serial.print(currentLidTemp);
      Serial.print(" ");
      Serial.print(currentFanPWM);
      Serial.print("\n");
    }
    if (verbosePID) {
      Serial.print(avgPTemp);
      Serial.print(" ");
      Serial.print(targetPeltierTemp);
      Serial.print(" ");
      Serial.print(peltierPWM);
      Serial.print("\n");
    }
    lastUIUpdateTime = millis();
  }
}

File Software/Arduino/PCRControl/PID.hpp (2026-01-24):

class PID {
  private:
    double kp, ki, kd;
    double outputMin, outputMax;
    double pError = 0, iError = 0;
    double lastDTerm = 0;      
    double iErrorLimit = 50; 
    unsigned long currentTime = 0, lastTime = 0;
    bool firstRun = true;

  public:
    PID(double pGain = 1, double iGain = 0, double dGain = 0,
        double minOut = -255, double maxOut = 255)
    {
      kp = pGain; ki = iGain; kd = dGain;
      outputMin = minOut; outputMax = maxOut;
    }

    void reset() {
      iError = 0; pError = 0; lastDTerm = 0;
      firstRun = true;
      lastTime = millis();
    }

    double calculate(double currentTemp, double targetTemp) {
      currentTime = millis();

      if (firstRun) {
        lastTime = currentTime;
        pError = targetTemp - currentTemp; 
        firstRun = false;
        return 0;
      }

      double dt = (currentTime - lastTime) / 1000.0;
      if (dt <= 0) dt = 0.001;
      lastTime = currentTime;

      double currentError = targetTemp - currentTemp;
      
      // Calculate Derivative term 
      double rawDTerm = kd * ((currentError - pError) / dt);
      
      // Filter the derivative
      double dAlpha = 0.8; 
      double dTerm = (dAlpha * lastDTerm) + ((1.0 - dAlpha) * rawDTerm);
      lastDTerm = dTerm;

      // Update pError for the next cycle
      pError = currentError;
      double provisionalOutput = (kp * pError) + (ki * iError) + dTerm;
      
      if (!((provisionalOutput > outputMax && pError > 0) || 
            (provisionalOutput < outputMin && pError < 0))) {
        iError += pError * dt; 
        iError = constrain(iError, -iErrorLimit, iErrorLimit);
      }

      // Final output
      double output = (kp * pError) + (ki * iError) + dTerm;
      return constrain(output, outputMin, outputMax);
    }
    // Setters
    void setKp(double value) { kp = value; }
    void setKi(double value) { ki = value; }
    void setKd(double value) { kd = value; }
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

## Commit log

2019-12-02 Added arduino comunication
2019-12-02 added commands for changing tempature and power
2019-12-12 Add files via upload
    PCR heating block
    [HeatBlock draft1.SLDDRW]
2020-01-07 notes on voltages
2020-01-08 added limits and current monitoring
2020-01-08 updated scripts and created cycleing power graph
2020-01-16 Heated lid data
2020-01-17 did some ananisys
    [pcrCycleTime.xlsx]
2020-01-18 did some ananysys
    [pcrCycleTime.xlsx]
2020-01-20 changed pin
2020-02-03 did some updates
    [Data.xlsx]
2020-02-03 Orginised git
    [HeatBlock draft1.SLDDRW, pcrCycleTime.xlsx]
2020-02-07 Recorded some calabration data might be bad
    [Data.xlsx]
2020-02-09 recorded new temperature data
2020-02-10 Did Temperature curve fit
2020-02-14 Applied Temperature calabration
2020-02-23 added temperature icon
2020-05-12 changed 'de' to an icon for backspace keys
2020-05-19 updated filtering may be too much
2020-05-21 started work in fixing PCRControl PID, Renamed Raspberry Pi folder to UI APP, Updated PCRDebugUI to somewhat work still dont reccomend using
2020-05-21 added FLC-PCR PCB rev 1
    [FLC-PCR PCB rev 1 Bill Of Matterials.xlsx, FLC-PCR PCB rev 1.brd, FLC-PCR PCB rev 1.sch]
2020-06-30 Started work on multy threadding serial comunication, should be a sutable workaround for the delays, needs to be tested
2020-09-08 started physical layout and modeling for NEMA enclosure
    [12711-9L31-10CQ.SLDPRT, FLC-PCR-NEMA.SLDASM, fs10040a-bracket.SLDPRT, md924a-12s-f1.SLDPRT]
2020-09-10 added solidwork files for hollow and solid heating block
    [HeatBlock_solid.SLDPRT, HollowBlock_v5.SLDPRT]
2020-09-10 Worked on NEMA enclosure
    [12711-9L31-10CQ.SLDPRT, FLC-PCR-NEMA.SLDASM, HollowBlock_v5.SLDPRT, Lid-Plate.sldprt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]
2020-09-24 finished first revision of lid
    [Body-Frame.SLDPRT, FLC-PCR-NEMA.SLDASM, Lid-Body.SLDPRT, Lid-Internal-Side.sldprt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]
2021-02-19 added photos of nema enclosure
2021-03-03 made small change to lid heating
2026-01-24 Updated TemperatureSensor class
    Added calculated Steinhart-Hart model coefficients to get better calibrated thermistor readings
    https://www.thinksrs.com/downloads/programs/therm%20calc/ntccalibrator/ntccalculator.html
2026-01-24 Updated PID class
    Optimized PID controller with signal filtering and improved error handling.
2026-01-24 Updated PID Controller
    Conditional PID values calibrated using the Ziegler–Nichols tuning method

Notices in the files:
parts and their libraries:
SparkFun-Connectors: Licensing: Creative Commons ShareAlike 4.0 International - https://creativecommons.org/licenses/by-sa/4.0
